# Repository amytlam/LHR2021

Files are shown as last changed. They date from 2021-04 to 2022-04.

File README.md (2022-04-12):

# LHR2021
This is the repository for the files associated with the paper "DIY Liquid Handling Robots for Integrated STEM Education and Life-Science Research".

This includes the following:
1. Hardware documentation:
    - Parts list
    - CAD source designs for mechanical parts
    - Laser cutting fabrication files (5 sheets)
    - Fabrication files for 3D printed parts
    - Electronic circuit schematic diagrams and CAD files
    - Assembly instructions
2. Software:
    - Low-level control software for Arduino
    - Python API and tools for tuning and calibration
    - Snap4Arduino visual programming environment

## Contents

The `hardware/` directory of this repository contains fabrication files and documentation for all hardware for the three-axis robot. CAD source designs for the mechanical components and subassemblies of the robot can be found in an associated [Onshape project](https://cad.onshape.com/documents/6f3ff9e60612f07463807b51/w/7c9831bb106114d48918156b/e/005c0d1900650c2e45e341be?renderMode=0&uiState=6254cec2aa34676ff2f642a7), which is made public for copying and exporting. These source designs were exported to create the cut patterns in `hardware/laser_cut_CAD_files/` and the 3D printing files in `hardware/3d_printed_CAD_files/`.

Source code and overview-level documentation of all software can be found at the associated repository [github.com/ethanjli/liquid-handling-robotics](https://github.com/ethanjli/liquid-handling-robotics).

## Usage

This hardware was developed and tested until October 2018 and is not currently maintained or supported. Troubleshooting and extensive technical skills will be needed to independently replicate the hardware design from the documentation provided in this repository, requiring deep familiarity with laser cutting, 3-D printing, assembly of simple printed circuit boards, and circuit prototyping.

### Mechanical Fabrication

Laser-cut parts, collected in the `hardware/laser_cut_CAD_files/annotated_laser_cutting_pdf_files.zip` file, are designed for 1/8-inch thick acrylic plates. Due to kerf and thickness variations among laser cutters and acrylic plates, the laser cutting patterns may need to be manually re-exported from the Onshape CAD source project after modifying the `kerfAdjustment` FeatureScript variable in the [`Design Parameters/Acrylic` tab](https://cad.onshape.com/documents/6f3ff9e60612f07463807b51/w/7c9831bb106114d48918156b/e/27868389b7af3fd50301f4c9) of the project.

Two units of the magnet hub, used in the x- and y-axis linear actuators of the robot, will need to be 3D printed using the `hardware/3d_printed_CAD_files/Magnet Hub (in).stl` file or the `hardware/3d_printed_CAD_files/Magnet Hub (mm).stl` file, depending on the length units used by the 3D printer. 

### Mechanical Assembly

Mechanical assembly can be performed following the photographs and notes in the `hardware/assembly_instructions/LHR Assembly of Laser Cut Parts.pdf` file.

Additionally, an 8mm x 2.50mm magnet, listed in the bill of materials, will need to be inserted into each 3D-printed magnet hub, and a magnet hub should be press-fitted to the D-shaped output shaft of the motor for each of the x- and y-axis linear actuators. A magnetic angle sensor printed circuit board (described below) should then be mounted to the linear actuator so that the angle sensor contacts the magnet.

### Circuit Assembly

The printed circuit board for the magnetic angle sensor, used in the x- and y-axis linear actuators of the robot, will need to be fabricated and assembled. Eagle CAD files and a zip archive of Gerber files can be found inside `hardware/electronic_circuits`, with filename `LHR Mag Sensor Mk2`.

For I2C switching of the magnetic angle sensor boards, a simple MOSFET circuit will need to be assembled (e.g. on a breadboard) from the schematic shown in the `hardware/electronic_circuits/LHR Circuit Diagrams.pdf` file.

Wiring and pin connections for the Arduino are shown in the `hardware/electronic_circuits/LHR Circuit Diagrams.pdf` file. Note that wires for the I2C signal lines must be kept as short as possible in order to mitigate radio frequency interference on those wires, which manifests as freezes in the Arduino software requiring a hard reset of the Arduino.

### Software Usage

Instructions for software setup and usage can be found in the README for [github.com/ethanjli/liquid-handling-robotics](https://github.com/ethanjli/liquid-handling-robotics#readme)

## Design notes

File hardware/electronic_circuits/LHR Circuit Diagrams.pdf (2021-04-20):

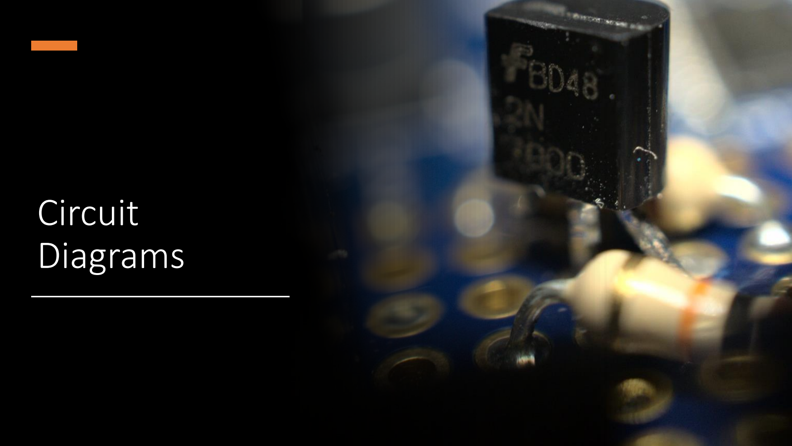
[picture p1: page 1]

# Circuit Diagrams

# Notes

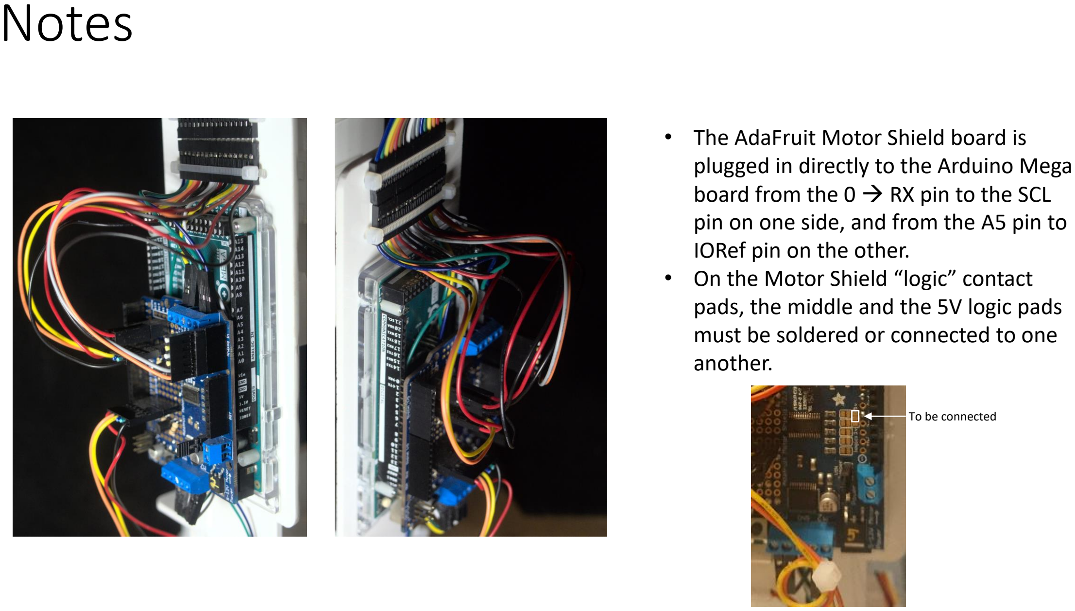
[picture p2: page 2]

- The AdaFruit Motor Shield board is plugged in directly to the Arduino Mega board from the 0

→ RX pin to the SCL
pin on one side, and from the A5 pin to IORef pin on the other.
- On the Motor Shield “logic” contact pads, the middle and the 5V logic pads must be soldered or connected to one another.

To be connected

# Circuit Diagrams: Sensors

Potentiometer | Magnetic Angle Sensors

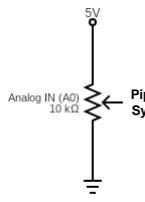
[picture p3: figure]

Pipettor
Syringe

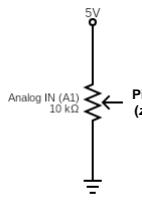
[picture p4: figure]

Pipettor
(z-axis)

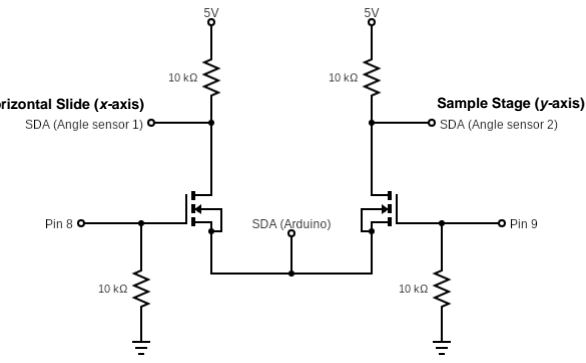
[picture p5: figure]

Horizontal Slide (x-axis) | Sample Stage (y-axis)

# Circuit Diagrams: Motors

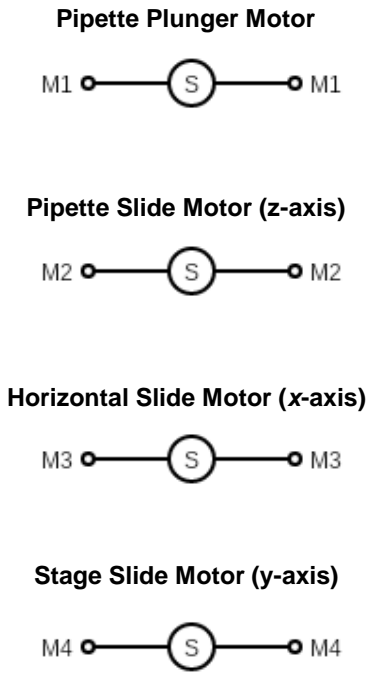
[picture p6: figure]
Pipette Plunger Motor; Pipette Slide Motor (z-axis); Horizontal Slide Motor (x-axis); Stage Slide Motor (y-axis)

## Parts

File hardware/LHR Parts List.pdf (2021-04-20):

Vendor | Item | # of Units URL
McMaster-Carr | Opaque Cast Acrylic Sheet | 5 | https://www.mcmaster.com/8505K741-8505K117/
McMaster-Carr | 1/4" Diameter Acetal Rod | 2 | https://www.mcmaster.com/8572K51/
Pololu | Mini Gearmotor, 80 RPM | 2 | https://www.pololu.com/product/1593
Pololu | Mini Gearmotor, 120 RPM | 2 | https://www.pololu.com/product/1511
Sparkfun | Large Slide Potentiometer | 2 | https://www.sparkfun.com/products/9119
Digikey | Angle Sensor | 2 | https://www.digikey.com/product-detail/en/ams/AS5601-ASOM/AS5601-ASOMCT-ND/5032390 (https://www.digikey.com/product-detail/en/ams/AS5601-ASOM/AS5601-ASOMCT-ND/5032390)
Sparkfun | Arduino Mega | 1 | https://www.sparkfun.com/products/11061
Adafruit | Shield Stacking Headers | 1 | https://www.adafruit.com/product/85
Adafruit | Adafruit Motor Shield | 1 | https://www.adafruit.com/product/1438
Digikey | I2C Switching Buffer | 1 | https://www.digikey.com/products/en/integrated-circuits-ics/interface-signal-buffers-repeaters-splitters/756?k=tca4311a&k=&pkeyword=tca4311a&pv7=2&pv16=6548&sf=0&quantity=&ColumnSort=0&page=1&pageSize=25 (https://www.digikey.com/products/en/integrated-circuits-ics/interface-signal-buffers-repeaters-splitters/756?k=tca4311a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)
Digikey | Diametric Magnet | 2 | https://www.digikey.com/product-detail/en/radial-magnet-inc/9050/469-1076-ND/6030787
Sparkfun | 8-Pin SOIC to DIP Adapter | 2 | https://www.sparkfun.com/products/13655
Jameco | 20-wire 8” M-F ribbon cable | 0.5 | https://www.jameco.com/z/ZW-MF-20-Busboard-Prototype-Systems-ZipWire-40-Piece-20cm-Male-to-Female-Colored-Jumper-Wires_2260754.html (https://www.jameco.com/z/ZW-MF-20-Busboard-Prototype-Systems-ZipWire-40-Piece-20cm-Male-to-Female-Colored-Jumper-Wires_2260754.html)
Digikey | SOIC TO DIP ADAPTER 8PIN 1=4 PCS | 1 | https://www.digikey.com/product-detail/en/sparkfun-electronics/BOB-13655/1568-1123-ND/5528943 (https://www.digikey.com/product-detail/en/sparkfun-electronics/BOB-13655/1568-1123-ND/5528943)
Digikey | TCA4311ADR I2C Buffer | 2 | https://www.digikey.com/products/en/integrated-circuits-ics/interface-signal-buffers-repeaters-splitters/756?k=tca4311a&k=&pkeyword=tca4311a&pv7=2&pv16=6548&sf=0&quantity=&ColumnSort=0&page=1&pageSize=25 (https://www.digikey.com/products/en/integrated-circuits-ics/interface-signal-buffers-repeaters-splitters/756?k=tca4311a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)
Digikey | 1µF ±10% 16V Ceramic Capacitor X8L 0603 | 2 | https://www.digikey.com/product-detail/en/tdk-corporation/CGA3E1X8L1C105K080AC/445-175260-1-ND/7930955 (https://www.digikey.com/product-detail/en/tdk-corporation/CGA3E1X8L1C105K080AC/445-175260-1-ND/7930955)
Digikey | Magnet Neodymium Iron Boron (NdFeB) N35SH 0.315" Dia x 0.098" H (8.00mm x 2.50mm) | 2 | https://www.digikey.com/product-detail/en/radial-magnet-inc/9050/469-1076-ND/6030787

Digikey | AS5601 Magnetic Position Sensor | 2 | https://www.digikey.com/product-detail/en/ams/AS5601-ASOM/AS5601-ASOMCT-ND/5032390 (https://www.digikey.com/product-detail/en/ams/AS5601-ASOM/AS5601-ASOMCT-ND/5032390)
Digikey | 10000pF ±10% 50V Ceramic Capacitor X7R Radial | 2 | https://www.digikey.com/product-detail/en/vishay-bc-components/K103K15X7RF53L2/BC5134-ND/2820436 (https://www.digikey.com/product-detail/en/vishay-bc-components/K103K15X7RF53L2/BC5134-ND/2820436)
Pololu | Breakaway Male Header: 1×40-Pin, Right Angle | 2 | https://www.pololu.com/product/967
Pololu | 1x2 Female Header, Straight | 2 | https://www.pololu.com/product/1012
Pololu | 6" Black M-F Jumpers | 5 | https://www.pololu.com/product/1720
Pololu | 6" Red M-F Jumpers | 5 | https://www.pololu.com/product/1722
Pololu | 6" Orange M-F Jumpers | 1 | https://www.pololu.com/product/1723
Pololu | 6" Yellow M-F Jumpers | 1 | https://www.pololu.com/product/1724
Pololu | 6" Green M-F Jumpers | 5 | https://www.pololu.com/product/1725
Pololu | 6" Blue M-F Jumpers | 5 | https://www.pololu.com/product/1726
Pololu | 6" Gray M-F Jumpers | 2 | https://www.pololu.com/product/1728
Pololu | 6" White M-F Jumpers | 2 | https://www.pololu.com/product/1729
Pololu | 12" Black M-F Jumpers | 3 | https://www.pololu.com/product/1750
Pololu | 12" Red M-F Jumpers | 3 | https://www.pololu.com/product/1752
Pololu | 12" Orange M-F Jumpers | 1 | https://www.pololu.com/product/1753
Pololu | 12" Yellow M-F Jumpers | 1 | https://www.pololu.com/product/1754
Pololu | 12" Green M-F Jumpers | 1 | https://www.pololu.com/product/1755
Pololu | 12" Blue M-F Jumpers | 1 | https://www.pololu.com/product/1756
Pololu | 12" Gray M-F Jumpers | 1 | https://www.pololu.com/product/1758
Pololu | 12" White M-F Jumpers | 1 | https://www.pololu.com/product/1759
Pololu | 2-pin connector housings | 2 | https://www.pololu.com/product/1910
Pololu | 4-pin headers | 2 | https://www.pololu.com/product/1014
Pololu | 6-pin headers | 1 | https://www.pololu.com/product/1016
Pololu | 8-pin headers | 1 | https://www.pololu.com/product/1018
Pololu | 18-pin headers | 8 | https://www.pololu.com/product/1656
Pololu | 3" Green M-F Jumpers | 1 | https://www.pololu.com/product/3315
Pololu | 3" Blue M-F Jumpers | 1 | https://www.pololu.com/product/3316

Note: Some vendors will only sell in units of >1 (e.g., the 6” Orange M-F Jumpers only come in sets of 2, so there would be one left over from the robot construction).

The vendors are only suggestions. It is not necessary to purchase the parts as listed if suitable alternatives are found.

Because of price fluctuations, the prices are not listed. The approximate price for one robot for the listed parts as of April 13, 2021 is about $150.

The vendors and URLs are current as of April 13, 2021.

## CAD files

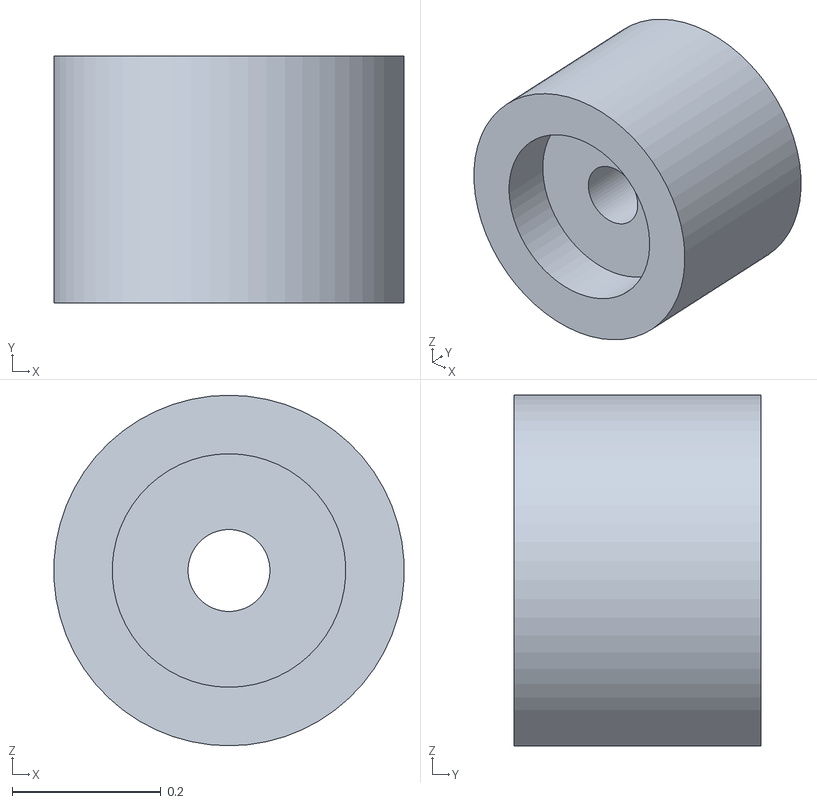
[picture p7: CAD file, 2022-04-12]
hardware/3d_printed_CAD_files/Magnet Hub (in).stl
0.471 x 0.333 x 0.472

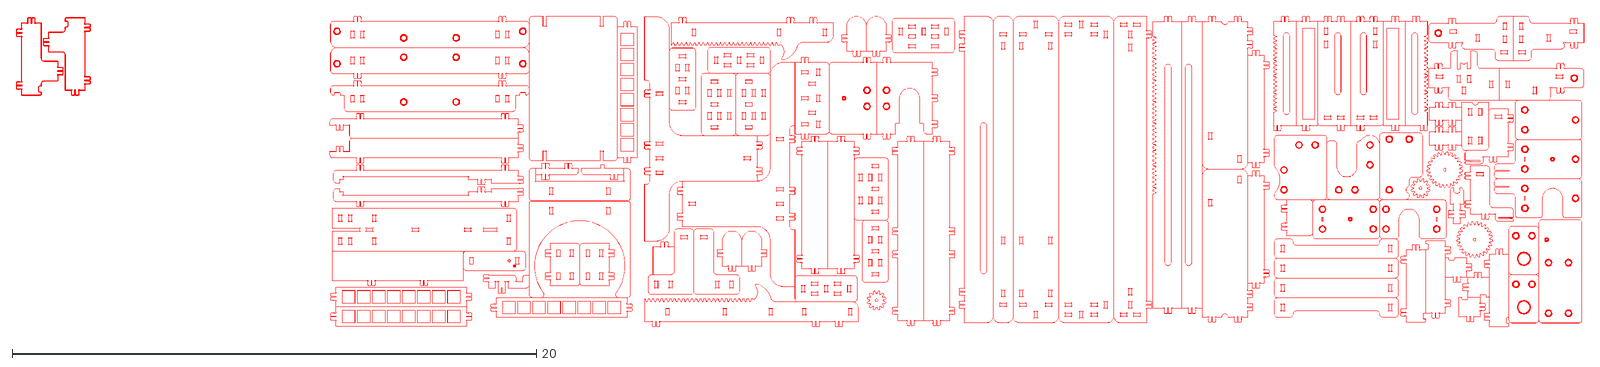
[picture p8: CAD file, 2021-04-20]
hardware/laser_cut_CAD_files/laser_cut_LHR_parts(all).dxf
59.8 x 11.8

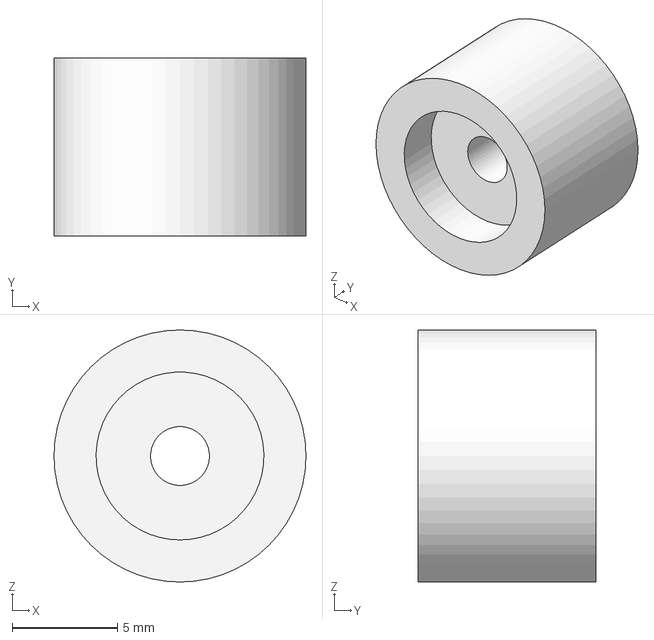
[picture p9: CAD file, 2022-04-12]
hardware/3d_printed_CAD_files/Magnet Hub.step
12.0 x 8.45 x 12.0 mm

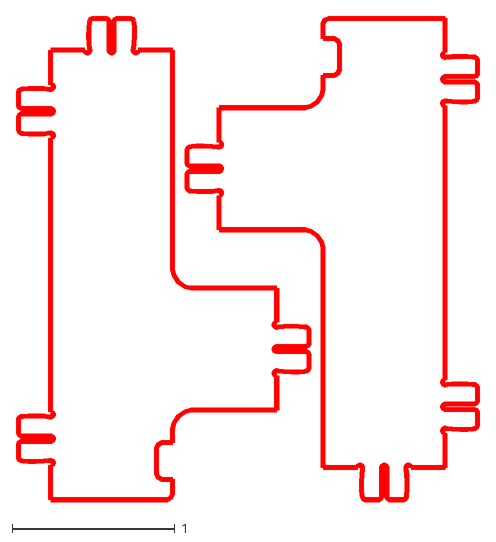
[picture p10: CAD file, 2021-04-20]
hardware/laser_cut_CAD_files/laser_cut_LHR_parts(sheet5).dxf
2.84 x 2.98

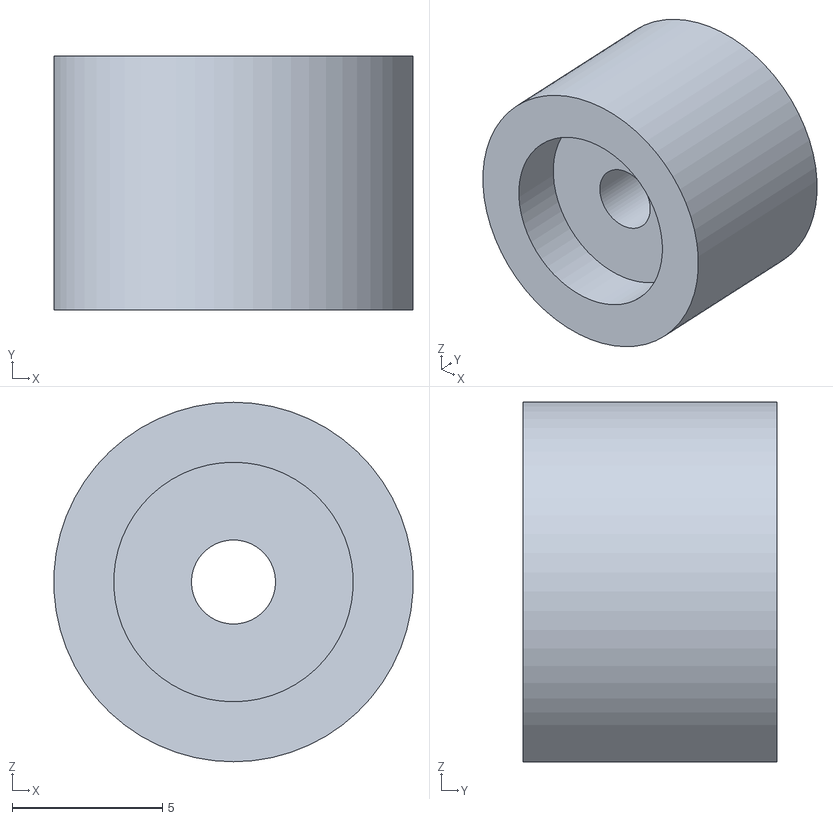
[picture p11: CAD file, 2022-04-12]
hardware/3d_printed_CAD_files/Magnet Hub (mm).stl
12.0 x 8.45 x 12.0

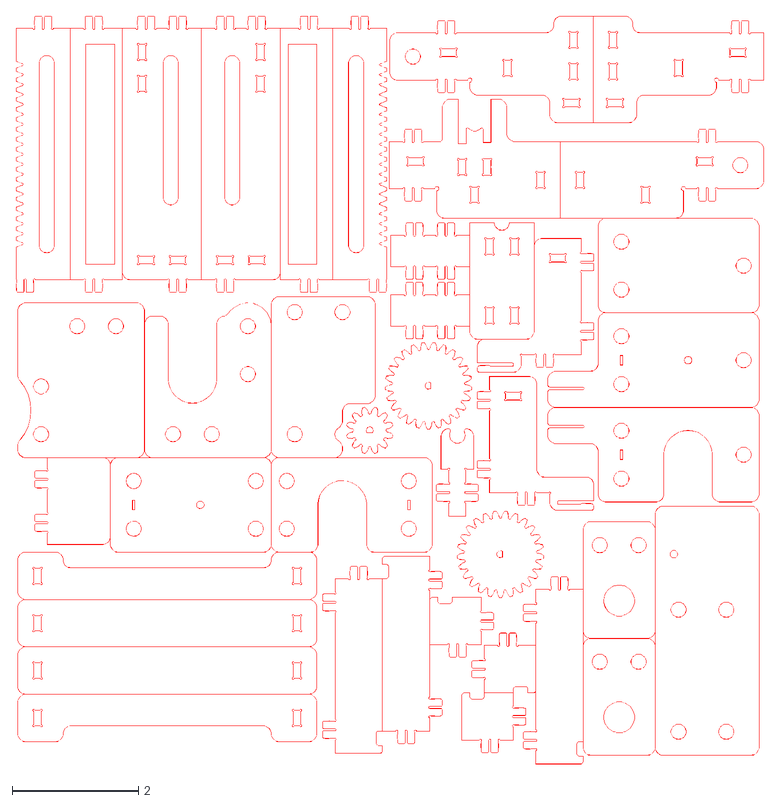
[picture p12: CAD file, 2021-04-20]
hardware/laser_cut_CAD_files/laser_cut_LHR_parts(sheet1).dxf
11.8 x 11.8

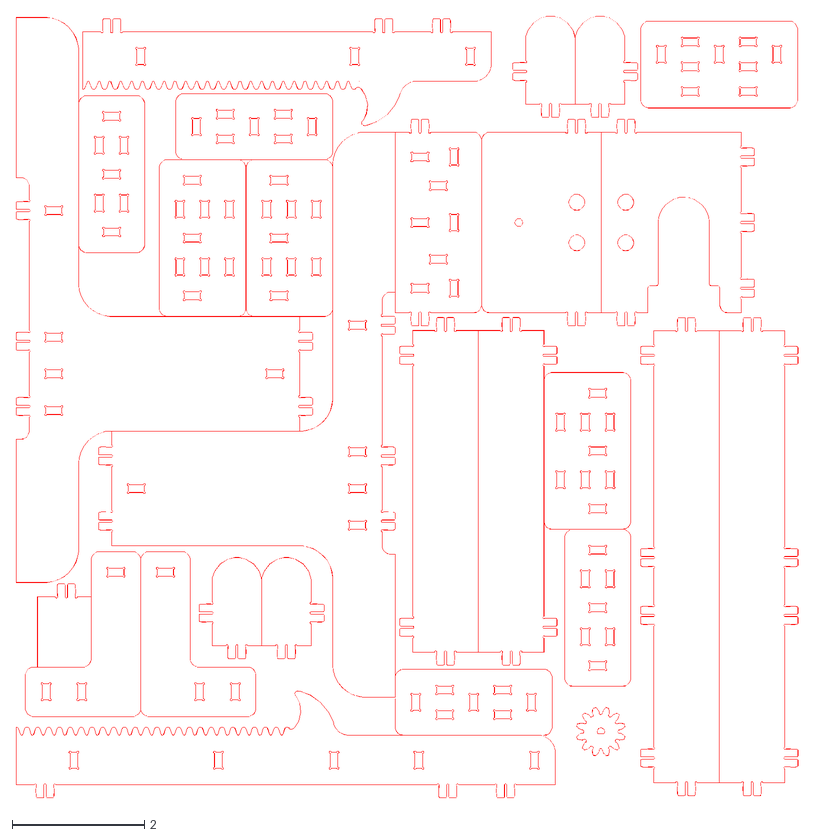
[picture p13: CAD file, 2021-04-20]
hardware/laser_cut_CAD_files/laser_cut_LHR_parts(sheet3).dxf
11.8 x 11.8

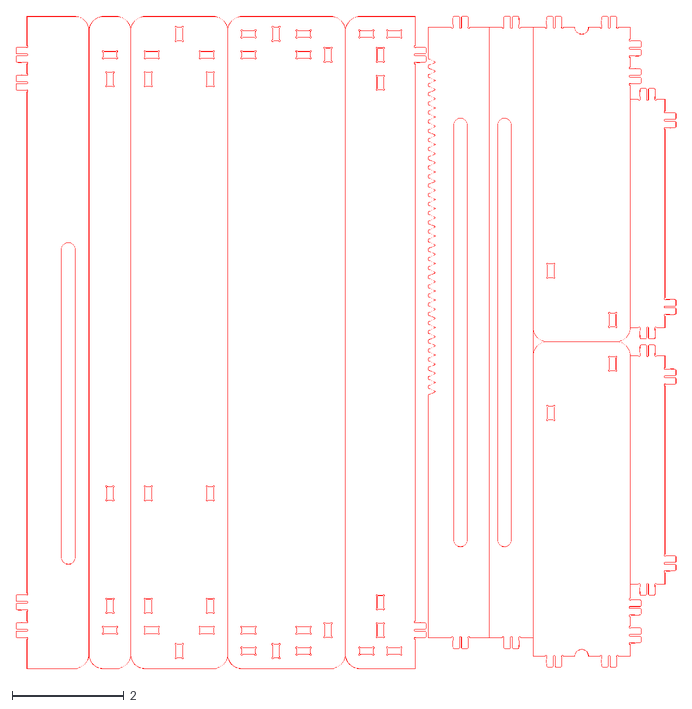
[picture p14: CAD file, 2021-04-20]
hardware/laser_cut_CAD_files/laser_cut_LHR_parts(sheet2).dxf
11.8 x 11.7

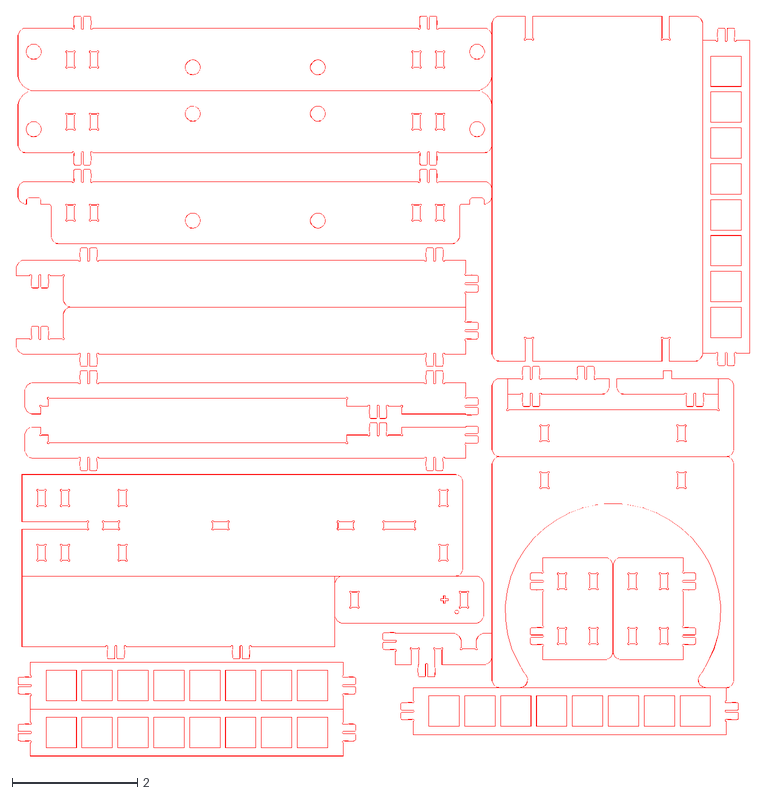
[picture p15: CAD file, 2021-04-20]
hardware/laser_cut_CAD_files/laser_cut_LHR_parts(sheet4).dxf
11.7 x 11.8

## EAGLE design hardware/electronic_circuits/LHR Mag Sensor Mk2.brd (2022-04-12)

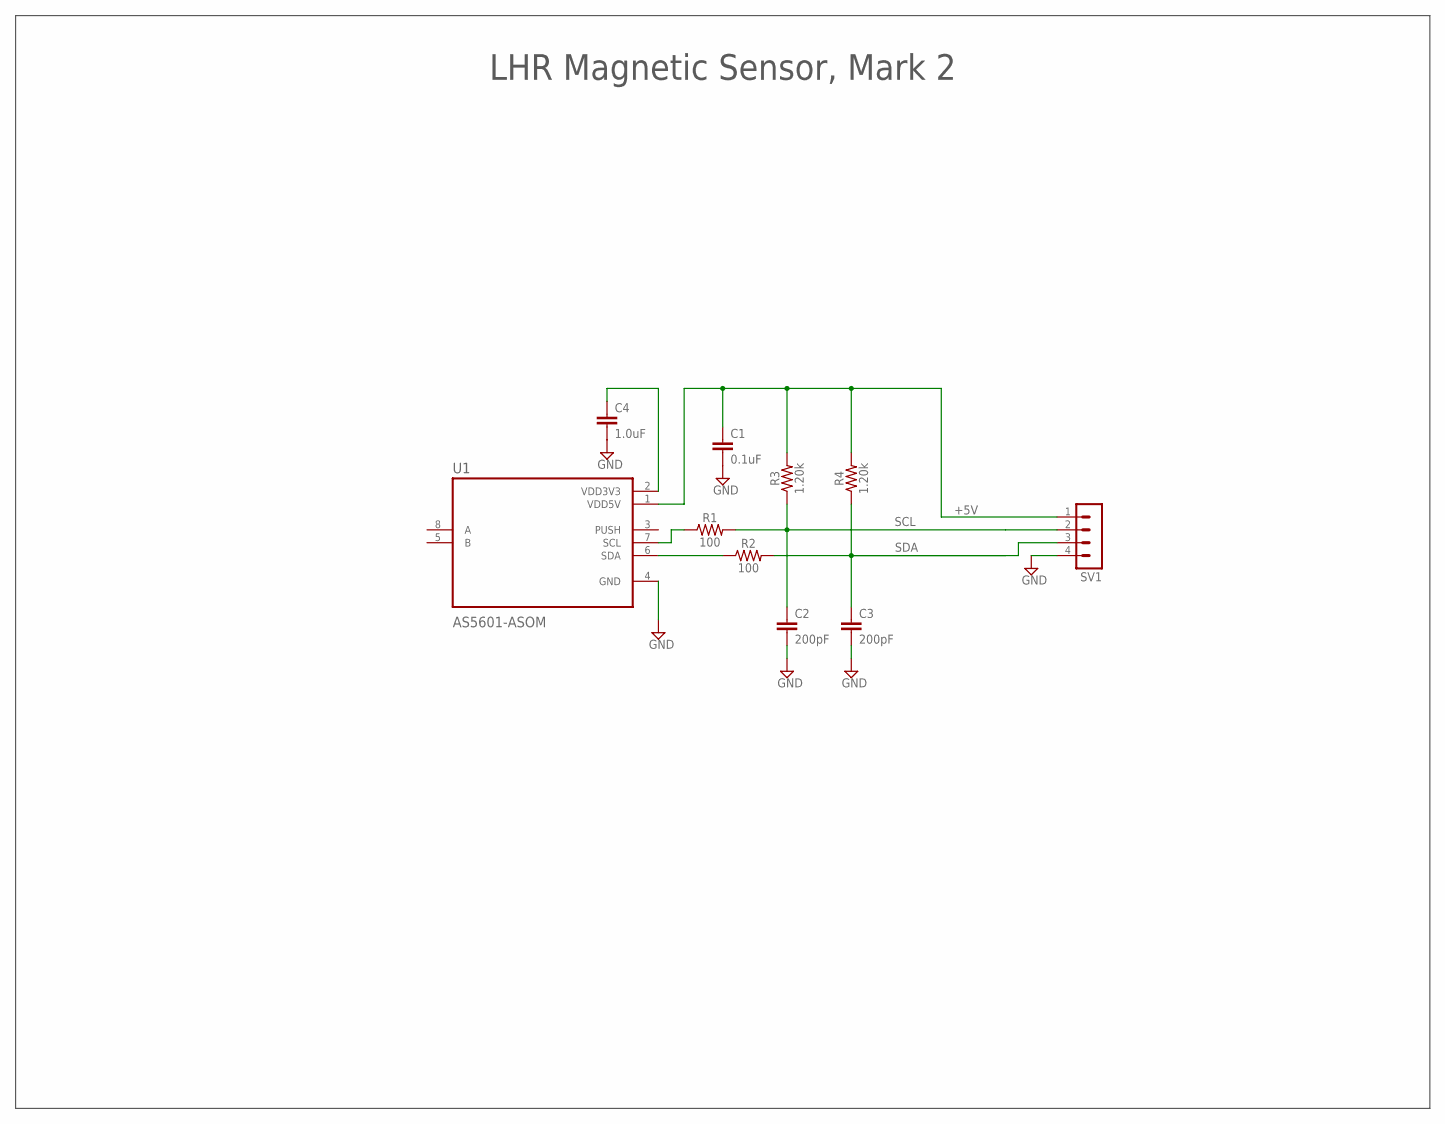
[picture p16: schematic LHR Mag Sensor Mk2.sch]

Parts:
C1: 0.1uF; 0603
C2, C3: 200pF; 0603
C4: 1.0uF; 0603
R1, R2: 100; 0603
R3, R4: 1.20k; 0603
SV1: MA04-1
U1: AS5601-ASOM; SOIC127P600X172-8N

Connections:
+5V: C1.1, R3.2, R4.2, SV1.1, U1.1 (VDD5V)
GND: C1.2, C2.2, C3.2, C4.2, SV1.4, U1.4 (GND)
unnamed: R2.1, U1.6 (SDA)
unnamed: C4.1, U1.2 (VDD3V3)
unnamed: R1.1, U1.7 (SCL)
SCL: C2.1, R1.2, R3.1, SV1.2
SDA: C3.1, R2.2, R4.1, SV1.3

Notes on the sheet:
LHR Magnetic Sensor, Mark 2

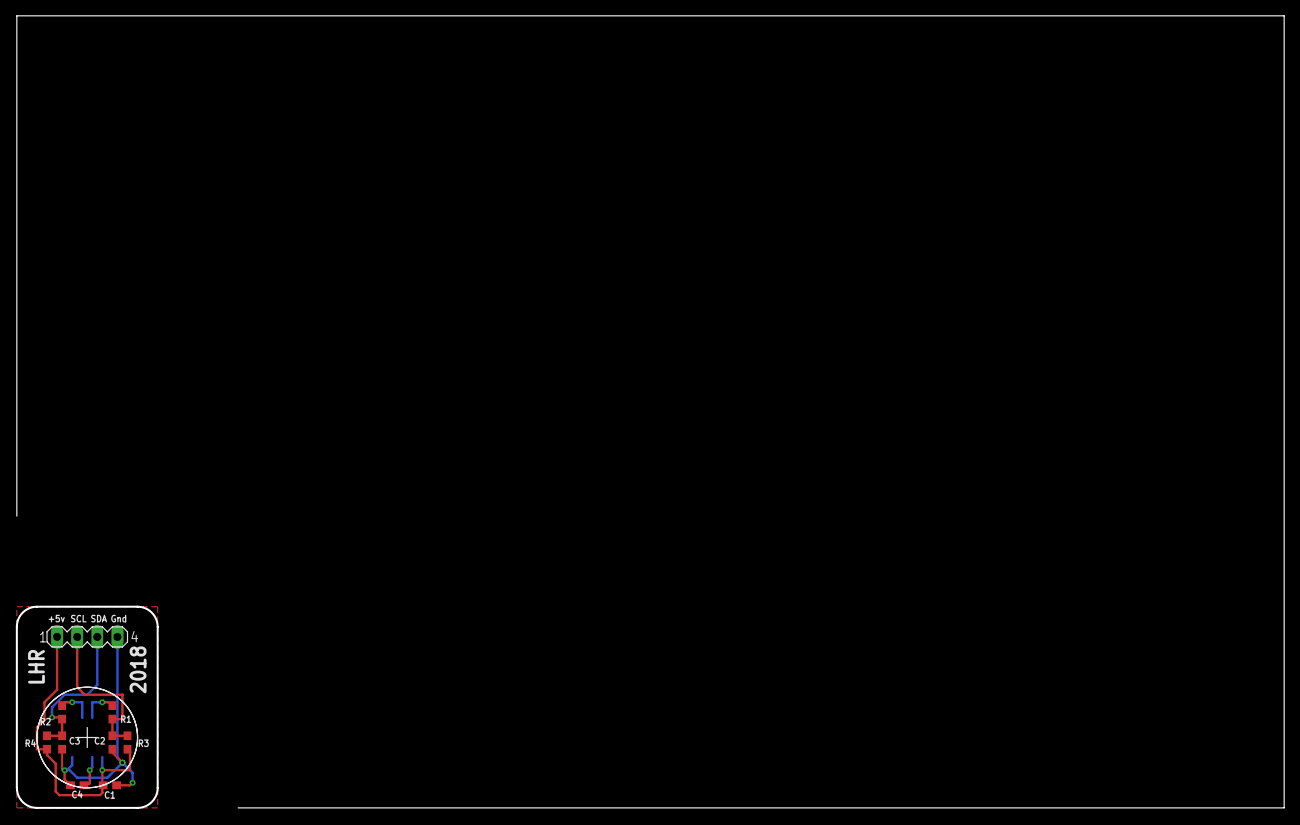
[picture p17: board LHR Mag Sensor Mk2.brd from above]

Board: 2 copper layers, 160.0 x 100.0 mm, 10 parts (1 on the bottom side), 7 nets.

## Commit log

2021-04-20 Add first set of files
    [laser_cut_LHR_parts(all).dxf, laser_cut_LHR_parts(sheet1).dxf, laser_cut_LHR_parts(sheet2).dxf, laser_cut_LHR_parts(sheet3).dxf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]
2022-04-12 Add more information to the README, add 3D printing files
    [Magnet Hub (in).stl, Magnet Hub (mm).stl, Magnet Hub.step]
2022-04-12 Add CAD and fab files for the angle sensor PCB
    [LHR Mag Sensor Mk2.brd, LHR Mag Sensor Mk2.sch]

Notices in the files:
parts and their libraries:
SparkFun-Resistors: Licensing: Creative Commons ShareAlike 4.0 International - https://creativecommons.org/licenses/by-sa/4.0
